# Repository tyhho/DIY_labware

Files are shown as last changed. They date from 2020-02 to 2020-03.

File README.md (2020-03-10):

# 3D Printable DIY Labwares

This is a repository for some DIY labwares which I have created to facilitate my experiments.

Every file comes in two formats - the original design that was drawn using DesignSpark Mechanical (.rsdoc) and the output file (.stl) which should be ready for print without any tweaks. 

## Aspirator Stand

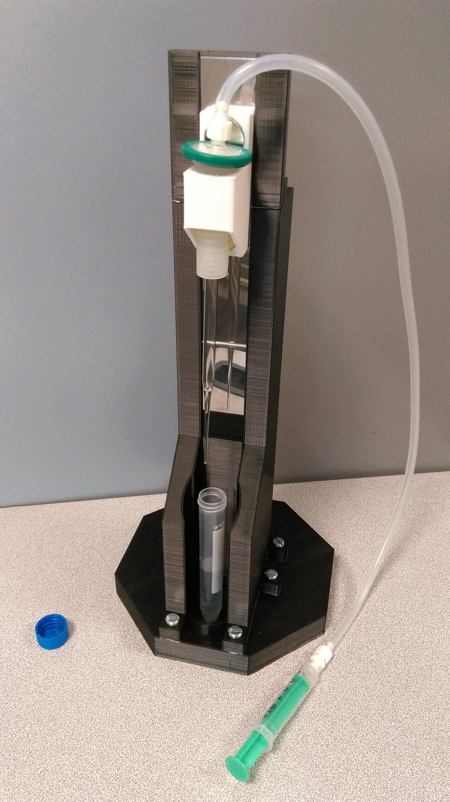
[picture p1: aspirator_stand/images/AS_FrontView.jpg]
Aspirator Stand Front View


This aspirator stand is designed to aid researchers who have the need to pipette a layer of liquid that was fractionated by centrifugation - a process which often the demands the pipetting to be done slowly and stably so as to avoid perturbing the fractionated layers.

Please open the folder ["aspirator_stand"](https://github.com/tyhho/DIY_labware/tree/master/aspirator_stand)  for more information.

## Colony Picking Assistant

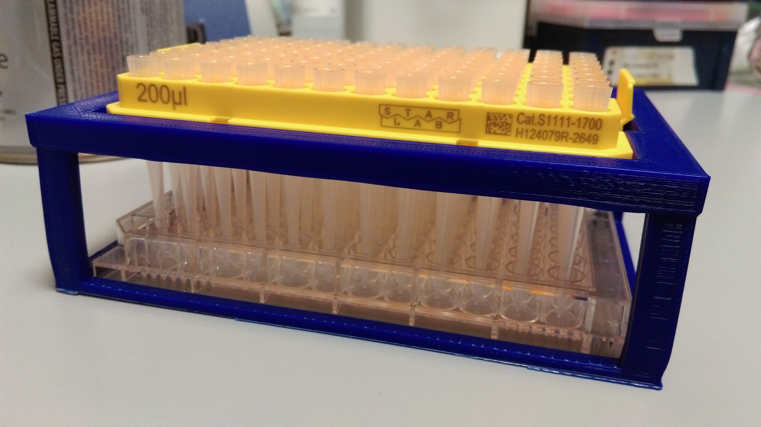
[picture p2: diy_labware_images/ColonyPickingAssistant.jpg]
Colony Picking Assistant Cover


A rack for tip rack insert to ease the process of manual colony picking. Please refer to its [wiki page](https://github.com/tyhho/DIY_labware/wiki/Colony-Picking-Assistant-(CFA)) for a full description and the recommended instructions.

Files:
* Colony Picking Assistant_200 uL tips & flat-bottom plates.stl

Recommended print setting: 20% infill, Triangle, Brim. Support (everywhere) is needed during printing.

## Universal Tube to 50 mL Tube Adaptor

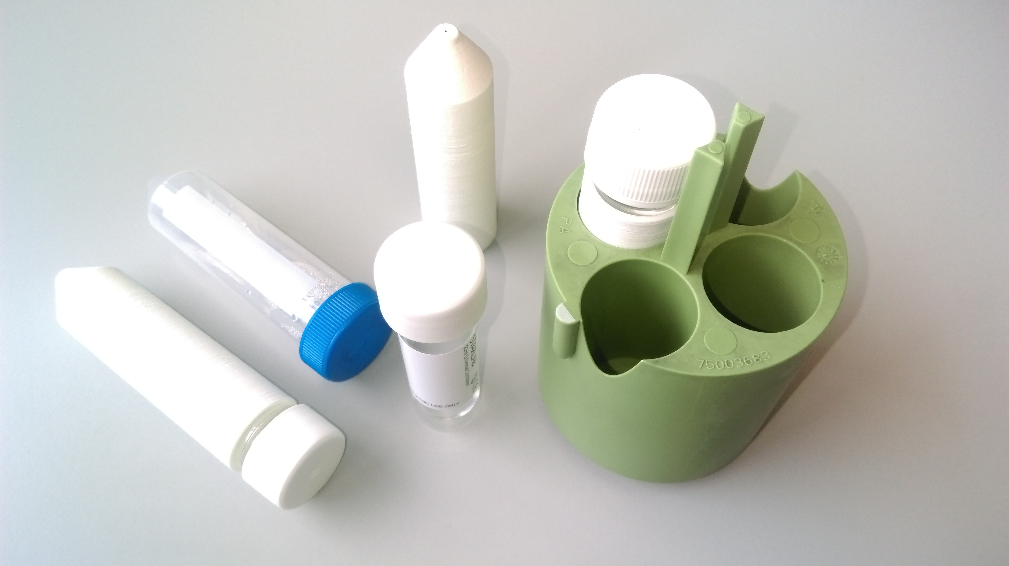
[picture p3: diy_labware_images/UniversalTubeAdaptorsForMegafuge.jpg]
Universal Tube to 50 mL Tube Adaptors


An adaptor to allow 30 mL Universal Tubes to fit into megafuge slots meant for 50 mL Falcon tubes.

Files:
* Universal Tube to 50 mL Tube Adaptor.stl

Recommended print setting: 20% infill, Triangle, Brim. Invert the design and print with support (everywhere).

##  50 mL Tube Vertical-to-horizontal Roller Adaptor

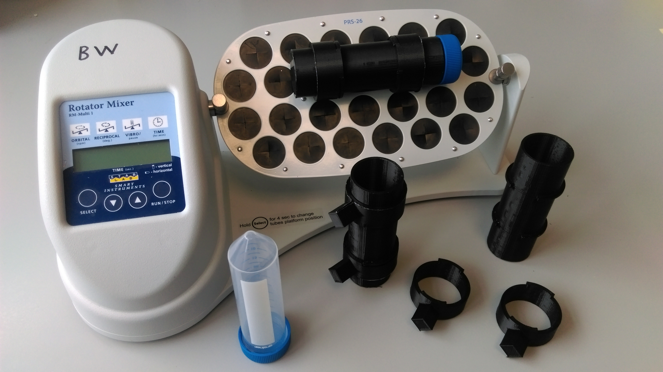
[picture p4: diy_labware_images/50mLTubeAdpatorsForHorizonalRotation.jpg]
50 mL Tube Adaptors For Horizontal Rotation


An adaptor to allow 50 mL Falcon tubes to be rotated horizontally and along the axis on a STARLAB Rotator Mixer (N2400-5000 + N2400-5103 / N2400-5104). In our lab we perform primary and secondary antibody incubation of Western Blot membranes inside the 50 mL tubes. This practice allows us to cut down the volume of the diluted antibody from 25+ mL (on a rocker) to 10 mL, and to save reagents over time.

To assemble a function adaptor, print two rings per body and slide the rings from the two sides of the body tube. Ensure the rings are locked properly.

Files:
* 50 mL Tube Vertical-to-horizontal Roller Adaptor_Body.stl
* 50 mL Tube Vertical-to-horizontal Roller Adaptor_Ring.stl

Recommended print setting: 20% infill, Triangle, Brim. Support (everywhere) is needed for both files.

##  Bio-Rad DNA Gel Comb Racks

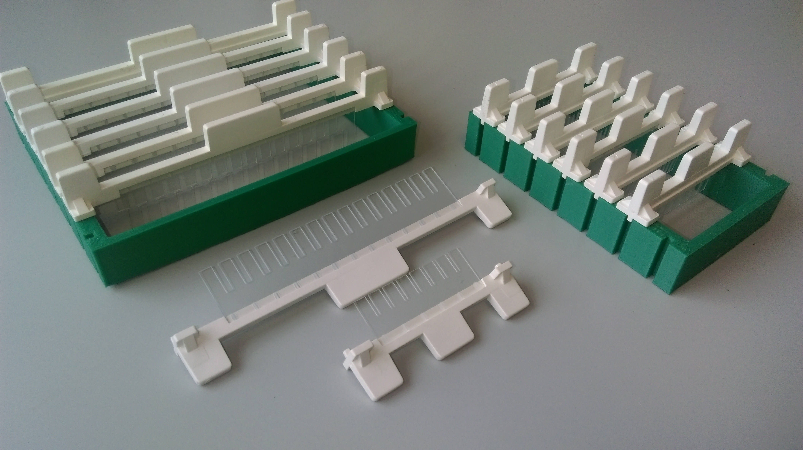
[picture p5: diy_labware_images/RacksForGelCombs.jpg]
Bio-Rad DNA gel comb racks


A rack to organize Bio-Rad DNA gel combs. This was designed to primarily allow the combs to air dry after wash. Additional benefits include creating a more organized gel running space and avoiding damaging combs when they stack on each other.

Files:
* Bio-Rad DNA Gel Comb Rack_Large_3slots.stl
* Bio-Rad DNA Gel Comb Rack_Large_7slots.stl
* Bio-Rad DNA Gel Comb Rack_Small_7slots.stl

Recommended print setting: 20% infill, Triangle, Brim.

## Acknowledgement

I thank Dr. Logan Mackay (Mass Spectrometry Facility, University of Edinburgh)  for providing access to a 3D printer.

## Questions/Issues/Suggestions
Please contact me through email since I do not actively or passively monitor my Github. Thank you.

## License
Licensed under the TAPR Open Hardware License (www.tapr.org/OHL)

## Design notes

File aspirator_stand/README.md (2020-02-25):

# Aspirator Stand

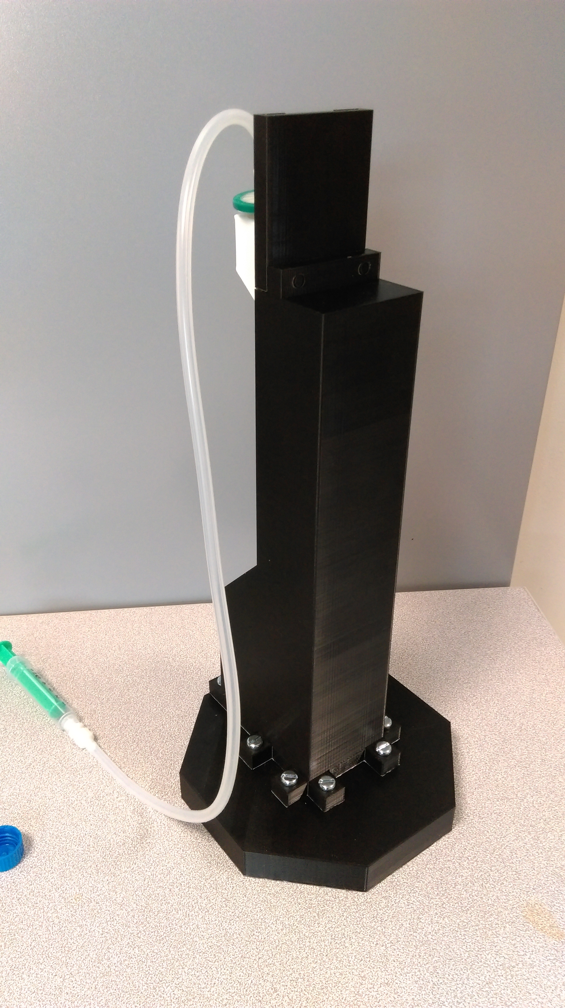
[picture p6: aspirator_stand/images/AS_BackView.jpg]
Aspirator Stand Back View
Aspirator Stand Front View 

## Introduction
This aspirator stand is designed to aid researchers who have the need to pipette a layer of liquid that was fractionated by centrifugation - a process which often the demands the pipetting to be done slowly and stably so as to avoid perturbing the fractionated layers.

Usually, a researcher will use a plastic Pasteur pipette / pipetteman with a tip attached. He/she will hold it steady above the tube while keeping the pressure on the piston / bulb, gradually low it so that the tip is submerged at the layer of interest, and then slowly releasing the piston / bulb while trying not to introduce motion that would disrupt the layers and cause remixing of the fractionated layers. This is an exacting procedure that requires quite an amount of skill and training. It is especially painstaking if the researcher has multiple samples that need to be processed in the same manner. 

This aspirator stand attempts to overcome this issue by "decoupling" the vertical motion of the pipette and the suction of the layer into two physically and temporally independent steps. When the aspirator is used, the researcher first places the centrifuged tube onto the designated slot on the **base** and removes that cap. The researcher then attaches an exchangeable glass pipette to an rubber insert, which hangs on the **lift** of the stand. The **lift** is held in place by magnets but can be slided up and down along a **magnetic rail (a magnetic steel sheet)**. The top of the glass pipette is connected air-tight to the rubber insert, then through a plastic tubing, to a syringe. Once the researcher set the Z-position of the glass pipette in place, he/she can then release hands from the **lift**, and then pull the syringe to suck up the liquid layer of interest without perturbing the Z-motion. Finally, the researcher pushes the **lift** upward, removes the source tube and replaces it with a collection tube, pushes the **lift** down again, and then pushes the syringe such that the pipetted liquid layer empties into the collection tube.

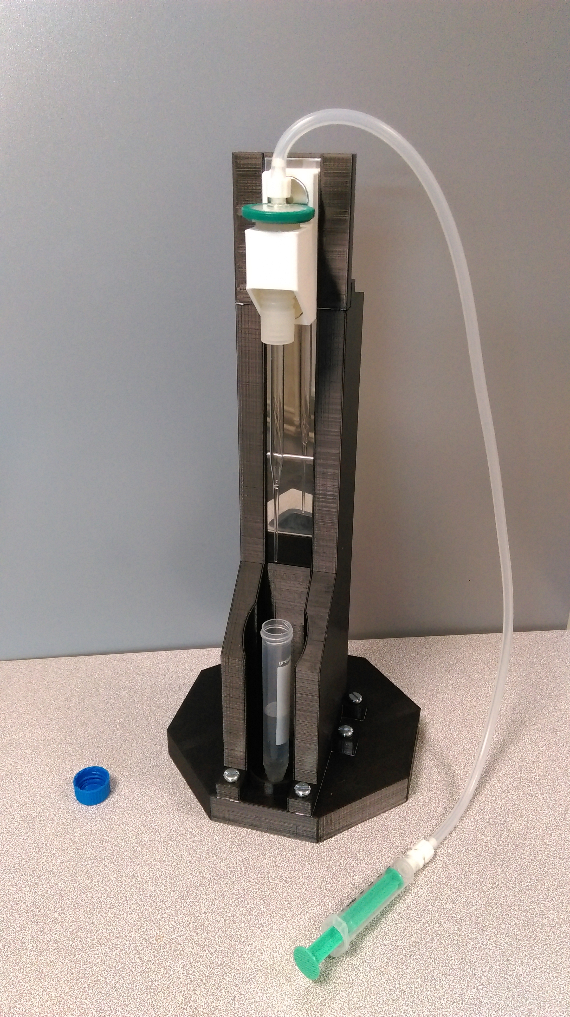
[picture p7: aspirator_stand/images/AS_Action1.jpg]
Aspirator Stand in action 1
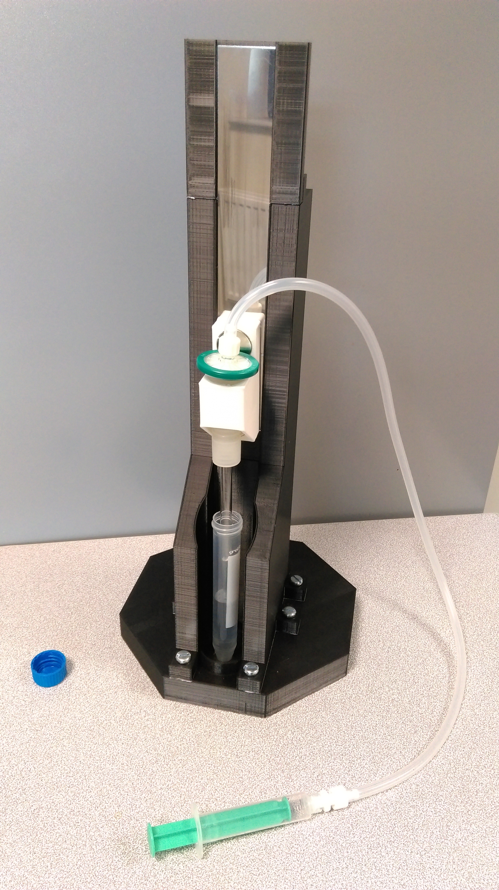
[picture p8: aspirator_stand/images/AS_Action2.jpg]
Aspirator Stand in action 2
 

The stand was primarily designed for a 15 mL Falcon centrifuge tube but should also work with a 50 mL Falcon centrifuge tube. To avoid cross contamination between samples and the tubings, a 22 µm filter is fitted between the adaptor and the tubing. This is identical to that most electronic pipette aids.

This invention was a response to a need mentioned in white blood cells extraction from whole blood, and has been successfully tested for that purpose.

## Materials
1. PLA Plastics for 3D Printing
2. M5 x 25 mm machine Screws and Nuts x 8
3. 150 * 50 * 2 mm 430 steel plate x 1
4. 50 * 50 * 2 mm 430 steel plate x 1
(note: the design could be modified to accommodate a single 300 * 50 * 2 mm steel plate, and any magnetic plates will do)
5. 20 mm diameter * 4 mm (5 mm hole) Neodymium disc round magnet x 4
6. 0.22 μm / 0.45 μm filter x 1
7. 3 mL syringe with Luer lock x 1
8. ~ 30 - 50 cm plastic tubing x 1
9. Connectors that join the filter and the Luer lock syringe to the plastic tubing
* Female Luer Union x 1
* Straight Male Luer Lock to Hose Barb Adapter x 2
10. Insert rubber that connects the glass Pasteur pipette / serological pipette to the filter and fits on the lift x 1. (Drummond Pipet-Aid Rubber Insert for EZ Grip Nosepiece is the one used here)

For the items #6 - #10, any combinations of products from different bands are acceptable as long as the joins are air-tight.

## Printing and Assembly
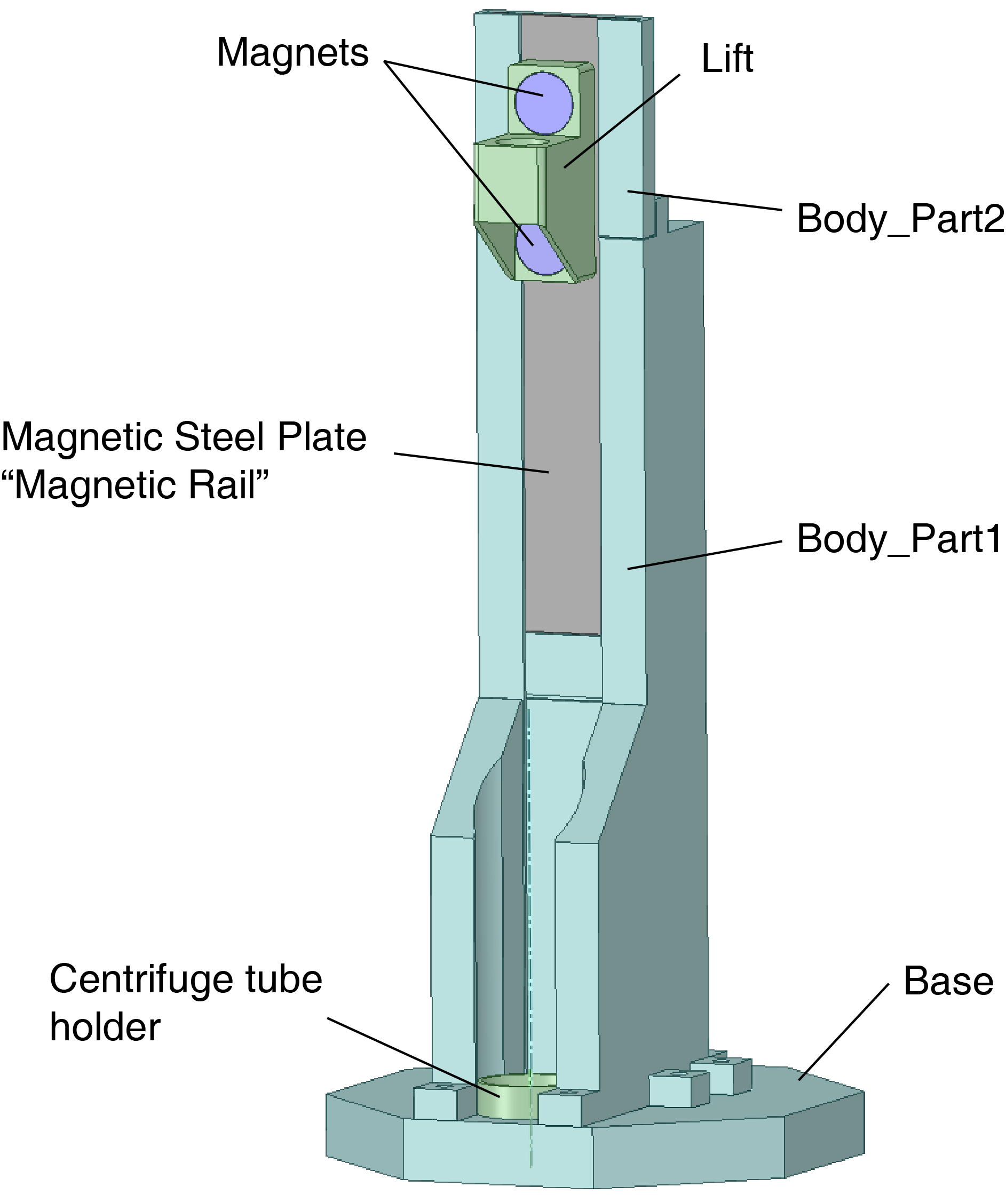
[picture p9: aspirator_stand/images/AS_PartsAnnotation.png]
Aspirator Stand parts annotated


* Recommended print setting: 40% infill, Cubic, Brim
* The **Base** and **Body_Part1** are assembled together via 8 screws and nuts. The direction of the nuts should not matter. If the holes for the screws were too tight, it might be necessary to drill them open a little.
* **Body_Part1** and **Body_Part2** must be joined prior to insertion of the magnetic steel into the socket. The 3D printed parts should snap to each other directly, like below:
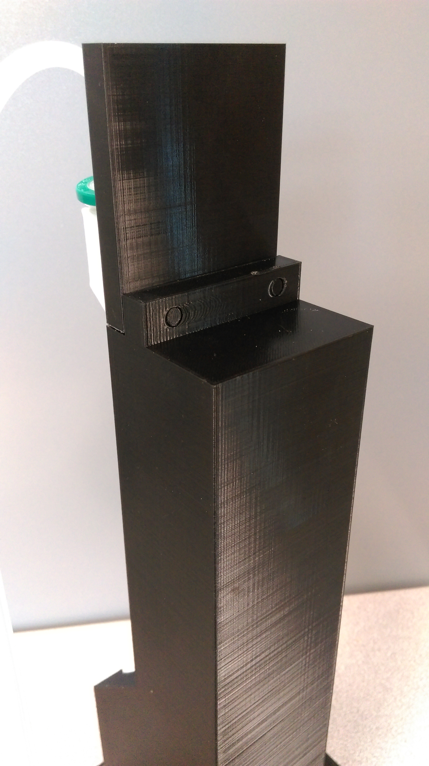
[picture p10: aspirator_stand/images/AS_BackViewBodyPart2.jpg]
Aspirator Stand Back View


* The design of the **lift** was specifically designed for the rubber insert from a broken pipette aid. Using a different substitute will necessitate a redesign of the **lift**.

## Known issues
1. If a 3D printer with print height > 30 cm is available, **Body_Part1** and **Body_Part2** could be merged as a single print object.
2. The initial workable design shown above considered the issue that the magnetic rail might be too high. This might happen if the liquid layer to pipette is located close to the bottom of the tube. A quick solution would be to remove the **spacing plastic** that stacks underneath the rail. This would shift the operable range of pipetting lower. However, a permanent solution would be to purchase a longer piece of magnetic steel sheets such that the entire range of height is covered. This might necessitate a corresponding adjustment in the 3D prints.

## Acknowledgement
Greg Sutton (iBioE, University of Edinburgh) described the need in repetitive white blood cells extractions from multiple samples.

Rose Rae (iBioE, University of Edinburgh) came up with the idea of salvaging the rubber insert from a broken pipette aid. Credits to her to make this stand feasible in the first place.

Dr. Logan Mackey (School of Chemistry, University of Edinburgh) provided access to a reliable 3D printing as well as materials, and set up print settings to yield the 3D parts shown here.

Dr. Abdelrahman Zaky kindly spared the plastic tubings and connectors for prototyping this aspirator stand.

## Questions/Issues/Suggestions
Please contact me through email since I do not actively or passively monitor my Github. Thank you.

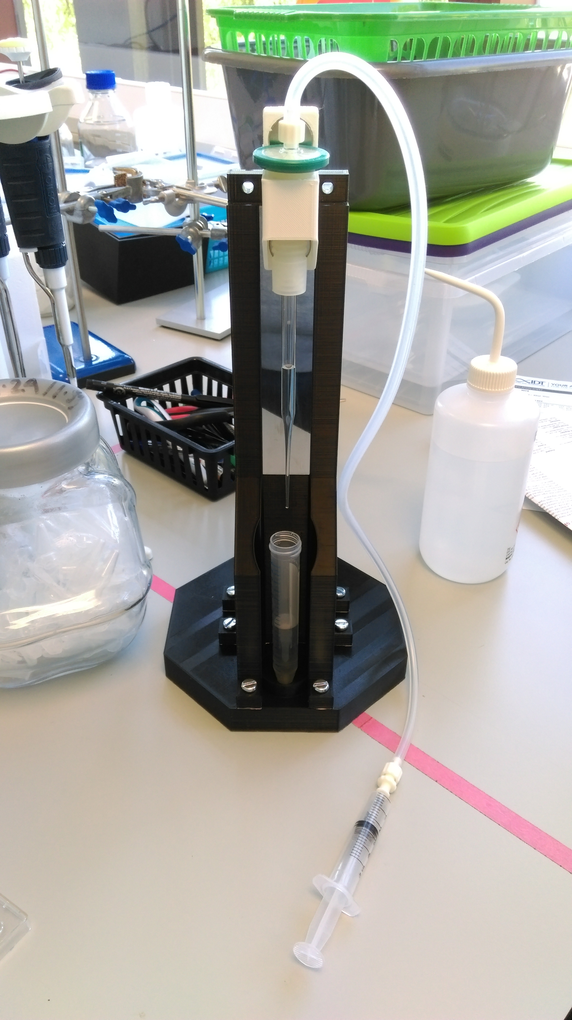
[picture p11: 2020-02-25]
aspirator_stand/images/AS_Part1Only.jpg

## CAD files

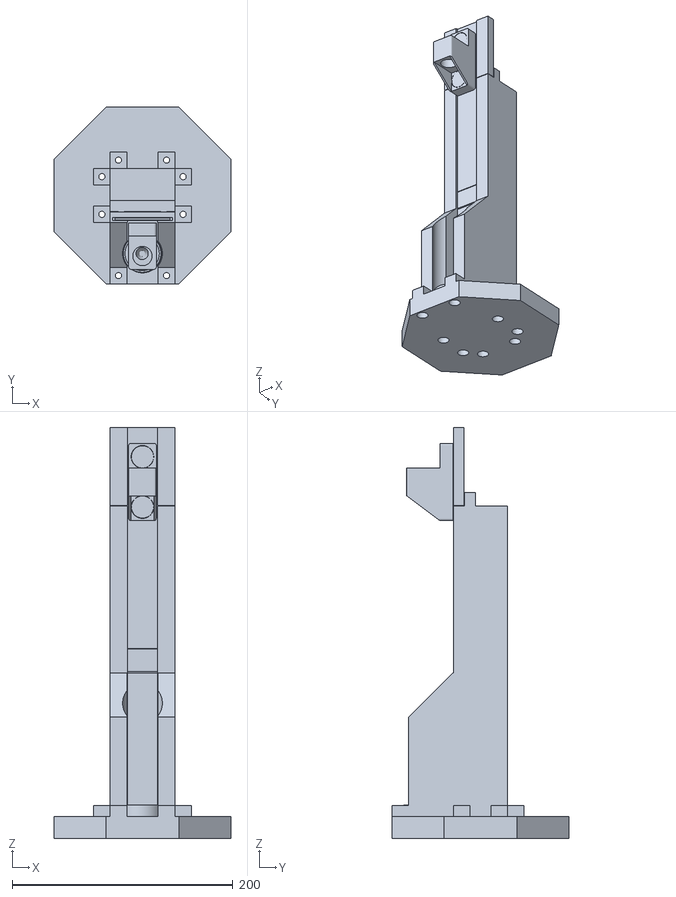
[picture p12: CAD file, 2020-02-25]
aspirator_stand/AspiratorStandAssembled.stl
160.0 x 160.0 x 372.0

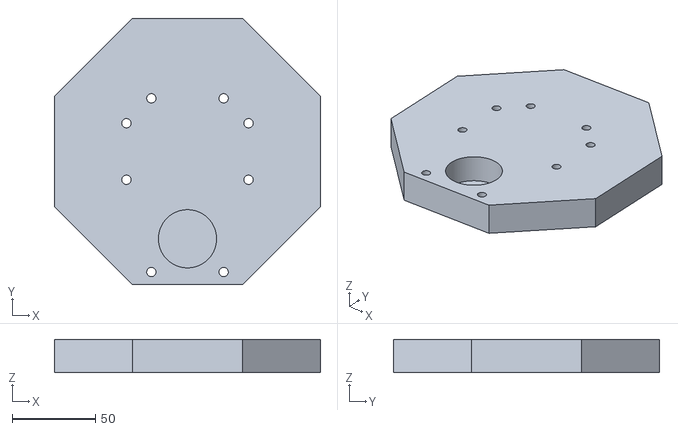
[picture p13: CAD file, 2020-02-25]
aspirator_stand/Base.stl
160.0 x 160.0 x 20.0

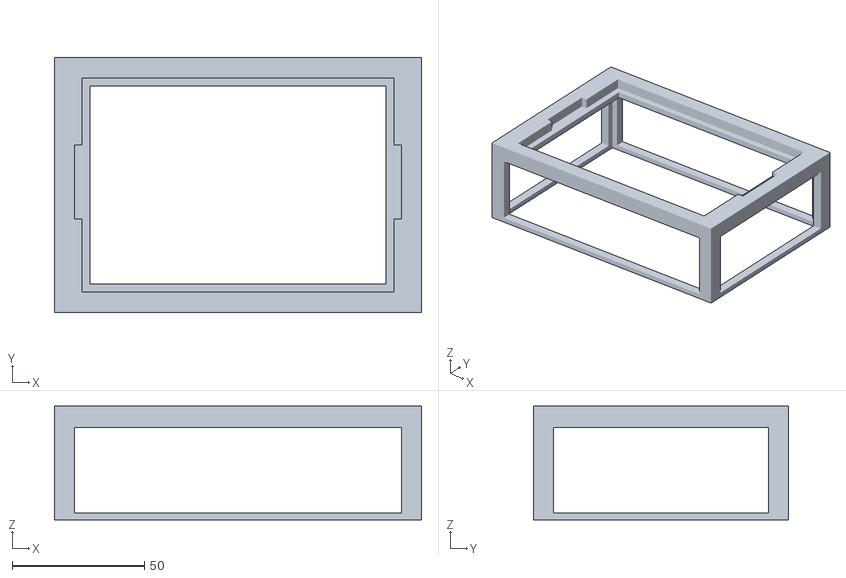
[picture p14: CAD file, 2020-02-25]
Colony Picking Assistant_200 uL tips & flat-bottom plates.stl
139.0 x 96.5 x 43.0

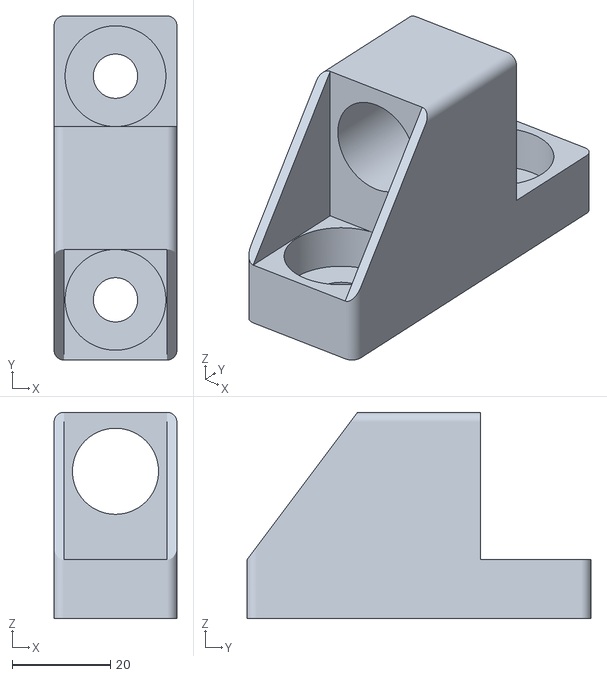
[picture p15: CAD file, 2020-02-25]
aspirator_stand/Lift Design D.stl
25.0 x 70.0 x 42.0

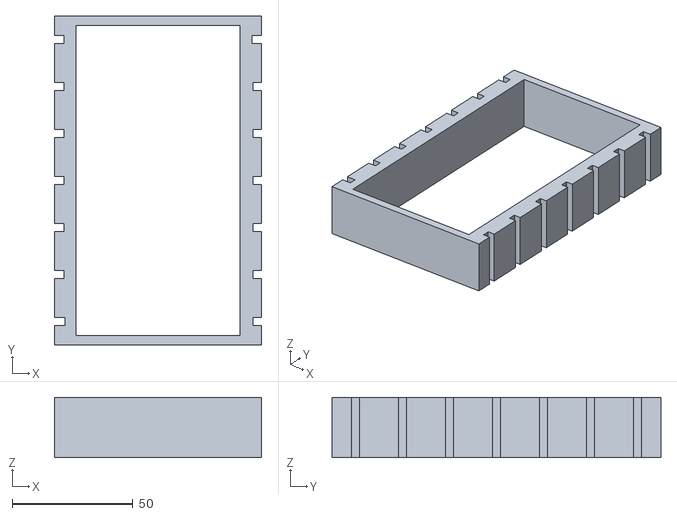
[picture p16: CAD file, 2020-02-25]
Bio-Rad DNA Gel Comb Rack_Small_7slots.stl
86.0 x 136.5 x 25.0

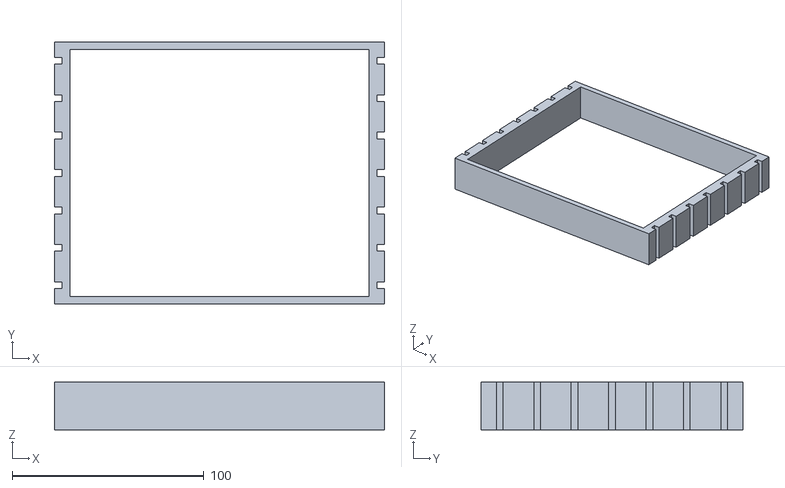
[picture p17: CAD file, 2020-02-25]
Bio-Rad DNA Gel Comb Rack_Large_7slots.stl
172.0 x 136.5 x 25.0

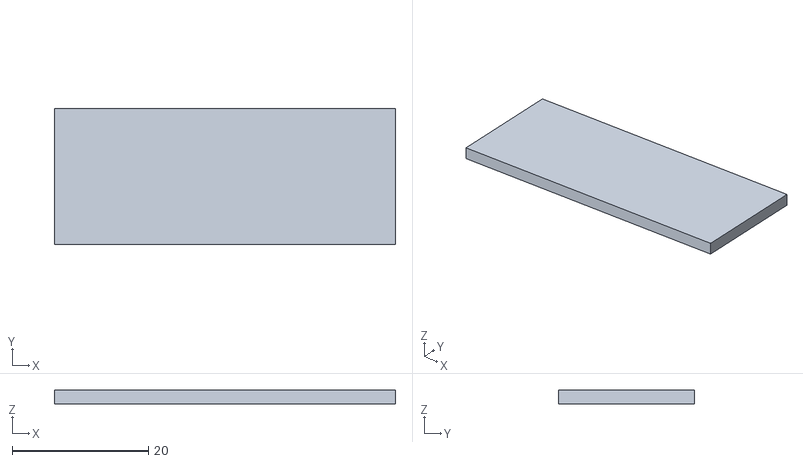
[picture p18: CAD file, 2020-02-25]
aspirator_stand/SpacingPlastic.stl
50.0 x 20.0 x 2.00

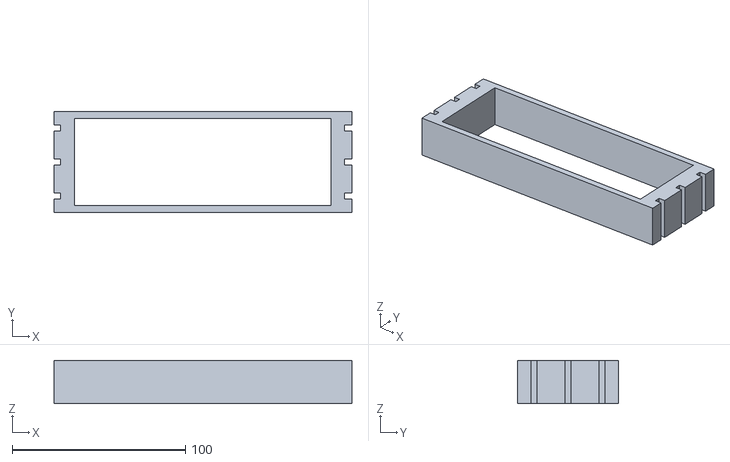
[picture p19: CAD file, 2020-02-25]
Bio-Rad DNA Gel Comb Rack_Large_3slots.stl
172.0 x 58.5 x 25.0

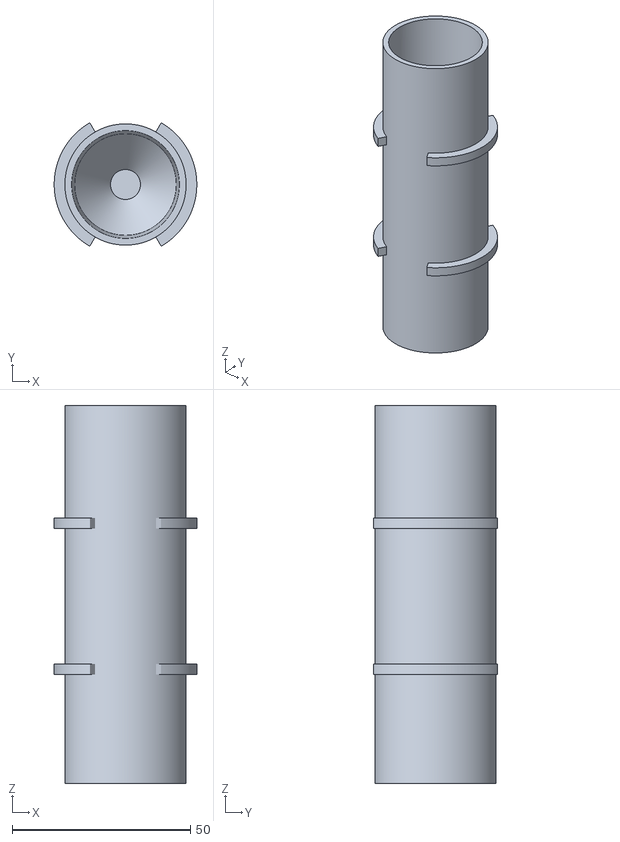
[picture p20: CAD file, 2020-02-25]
50 mL Tube Vertical-to-horizontal Roller Adaptor_Body.stl
40.0 x 34.6 x 106.0

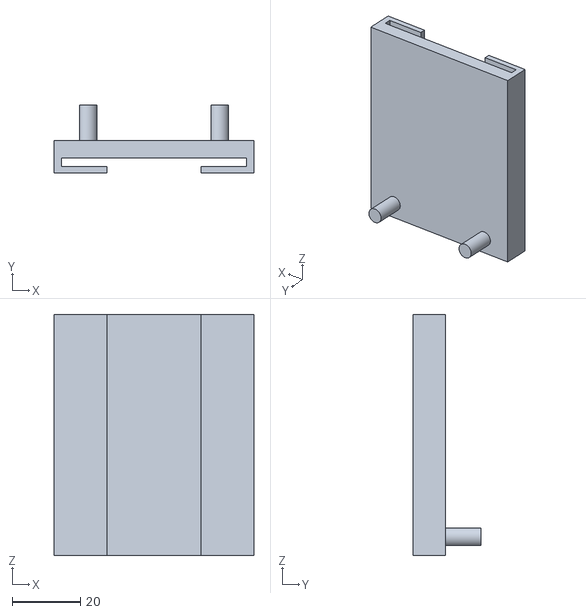
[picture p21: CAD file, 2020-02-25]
aspirator_stand/Body_Part2.stl
58.5 x 20.0 x 70.5

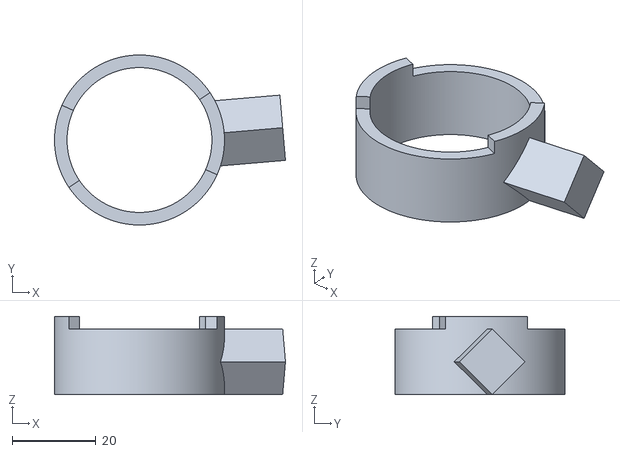
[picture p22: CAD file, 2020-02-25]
50 mL Tube Vertical-to-horizontal Roller Adaptor_Ring.stl
55.0 x 40.5 x 18.6

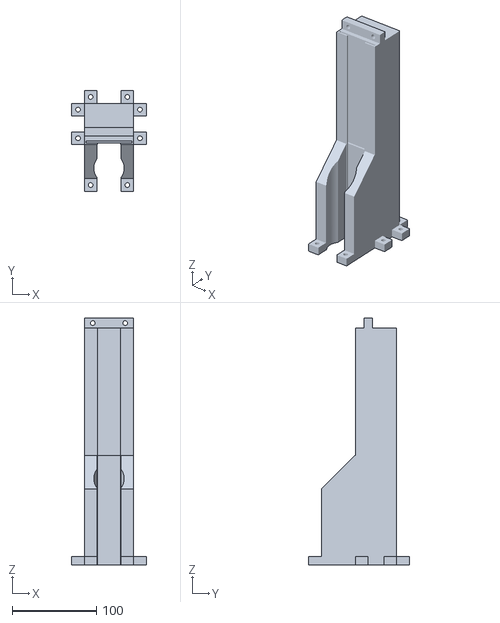
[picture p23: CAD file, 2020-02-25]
aspirator_stand/Body_Part1.stl
88.5 x 119.5 x 293.0

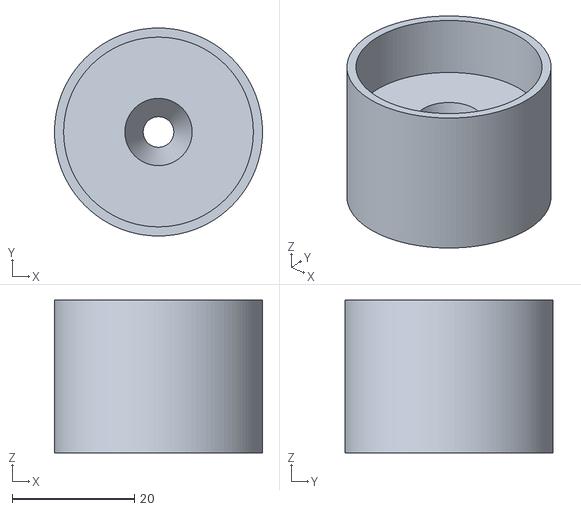
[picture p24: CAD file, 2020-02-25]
aspirator_stand/CentrifugeTubeHolder.stl
34.0 x 34.0 x 25.0

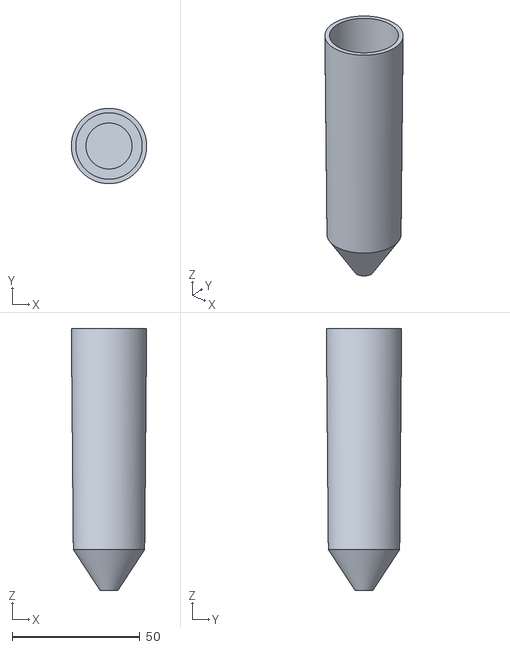
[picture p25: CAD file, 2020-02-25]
Universal Tube to 50 mL Tube Adaptor.stl
29.5 x 29.5 x 102.6

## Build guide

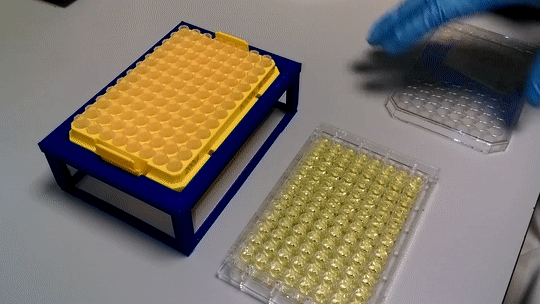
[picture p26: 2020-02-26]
diy_labware_images/CFA_Step3.gif

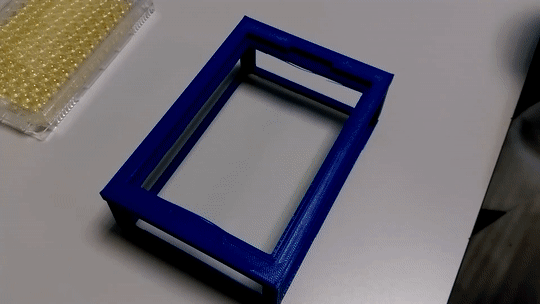
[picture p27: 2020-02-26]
diy_labware_images/CFA_Step1.gif

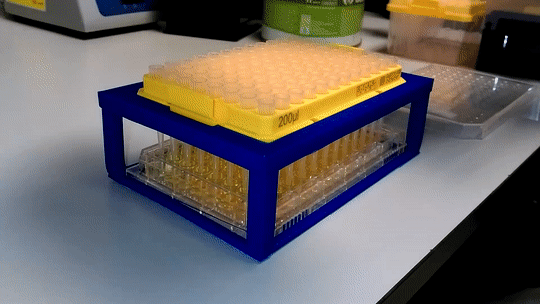
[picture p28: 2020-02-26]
diy_labware_images/CFA_Step5.gif

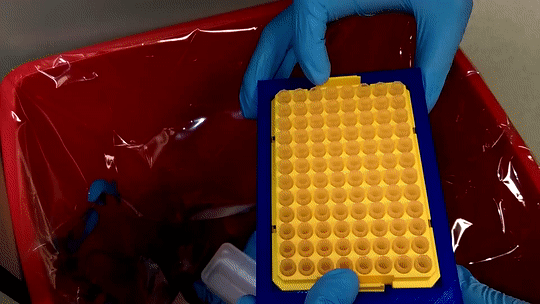
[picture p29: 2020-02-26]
diy_labware_images/CFA_Step6.gif

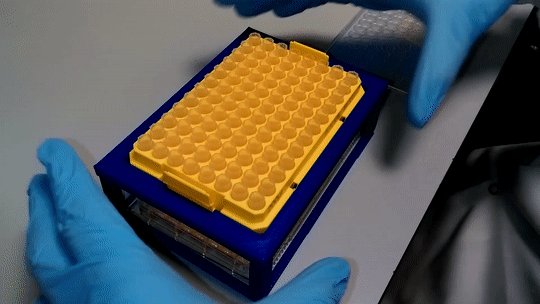
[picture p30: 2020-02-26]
diy_labware_images/CFA_Step4.gif
